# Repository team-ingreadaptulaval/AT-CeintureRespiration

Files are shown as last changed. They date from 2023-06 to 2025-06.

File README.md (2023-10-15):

# CeintureRespiration





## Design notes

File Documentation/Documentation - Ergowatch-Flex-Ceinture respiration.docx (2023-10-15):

### Carte principale

Pin arduino | Connection interne | Description
D0 | BTN4 (pas de pull-up)* | Bouton sur le PCB
D1 | BTN3 (pas de pull-up)* | Bouton sur le PCB
D2 | LED1 | LED sur le PCB
D3 | LED2 | LED sur le PCB
D4 | SD_DETECT | Carte SD insérée
D5 | EXT4 | Groove J2 pin 2
D6 | OLED_RST | Écran OLED et carte SD
D7 | OLED_CS | Écran OLED et carte SD
D8 | BUZZER | Buzzer sur le PCB
D9 | OLED_DC | Écran OLED et carte SD
D10 | SD_CS | Chip Select carte SD
D11 | SPI_MOSI | Écran OLED et carte SD
D12 | SPI_MISO | Écran OLED et carte SD
D13 | SPI_CLK | Écran OLED et carte SD
A0 | Batt_Voltage | diviseur de tension par 11
A1 | EXT1 | Groove J1 pin 1
A2 | EXT2 | Groove J1 Pin2
A3 | EXT3 | Groove J2 pin 1
A4 | SDA | Groove J3 pin 2
A5 | SCL | Groove J3 pin1
A6 | BTN1 (pas de pull-up)* | Bouton sur le PCB
A7 | BTN2 (pas de pull-up)* | Bouton sur le PCB
Vin | Batterie 9V | Alimente le arduino

*Utiliser la commande pinMode en INPUT_PULLUP

## Module d’expansion

Pin expansion | Connection | Module ceinture respiration
1 | GND
2 | VBAT | Recoit entre 4.5V et 9V
3 | EXT1 - A1 | Ceinture 1
4 | EXT2 - A2 | Ceinture 2
5 | EXT3 - A3
6 | EXT4 - D5
7 | SDA - A4
8 | SCL - A5
9 | 3V3
10 | 5V

## Carte Arduino installée

Carte 1 – Fabriquée le 23 septembre 2023

Arduino nano 33 sense REV2 –

https://docs.arduino.cc/hardware/nano-33-ble-sense-rev2

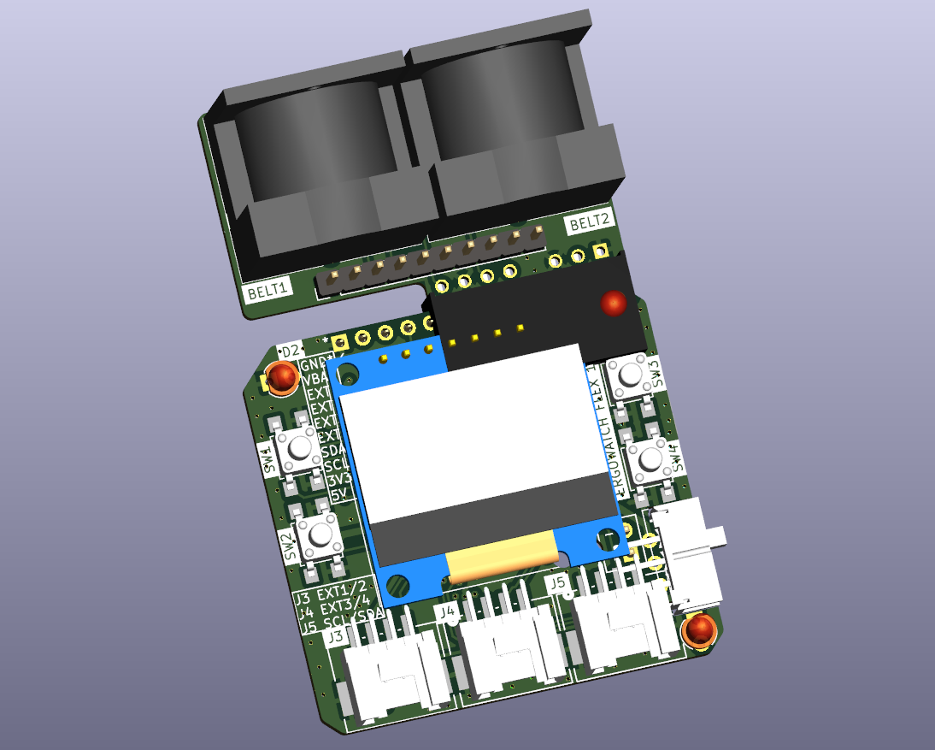
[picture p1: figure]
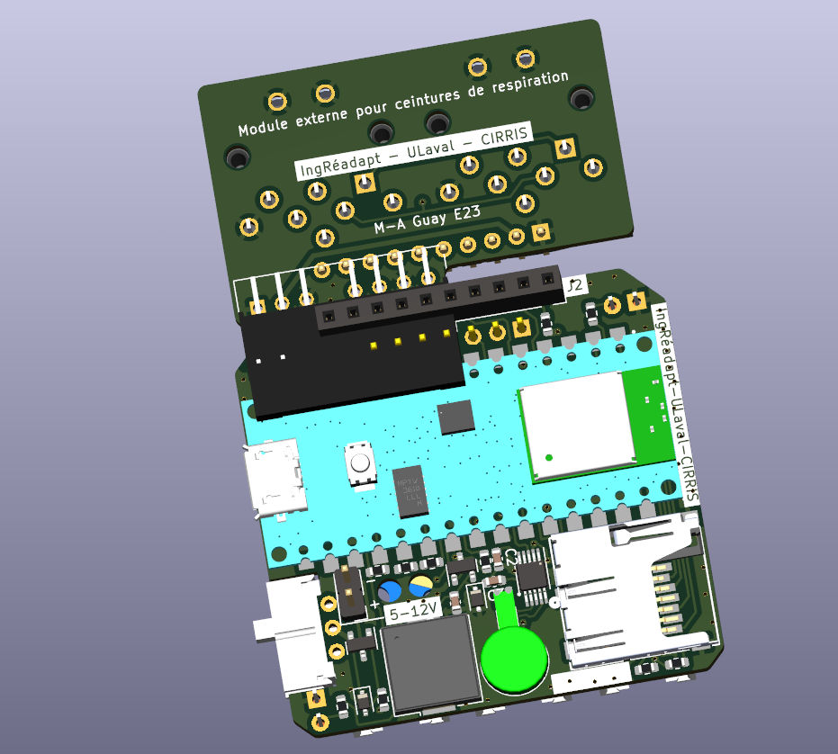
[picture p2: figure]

Documentation Ergowatch flex (Motherboard ceinture respiration)

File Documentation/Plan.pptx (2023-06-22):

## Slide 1

Batterie 12V

Bout on/off

Bout

LED

PQDE6W-Q24-D5-T

Bout

LED pwr

Connect
DIN

Arduino Nano 33 BLE

DRV &
VIB

Carte
SD

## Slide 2

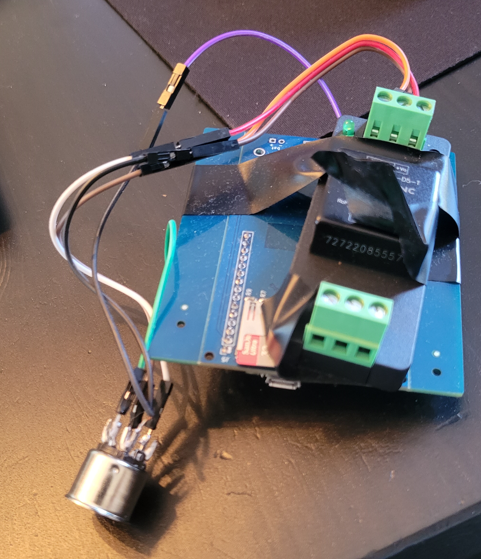
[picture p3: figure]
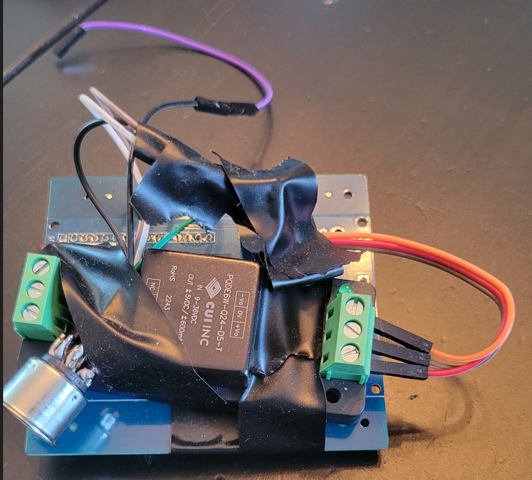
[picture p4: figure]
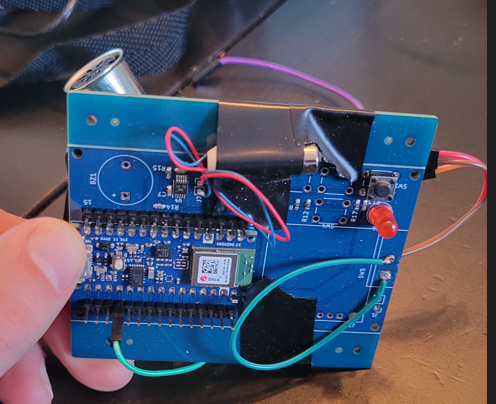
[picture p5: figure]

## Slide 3

GND arduino

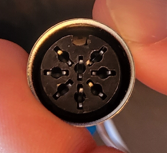
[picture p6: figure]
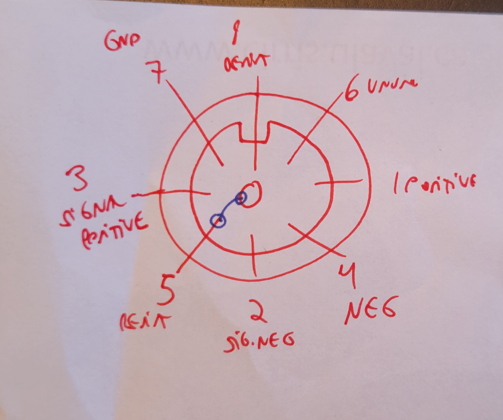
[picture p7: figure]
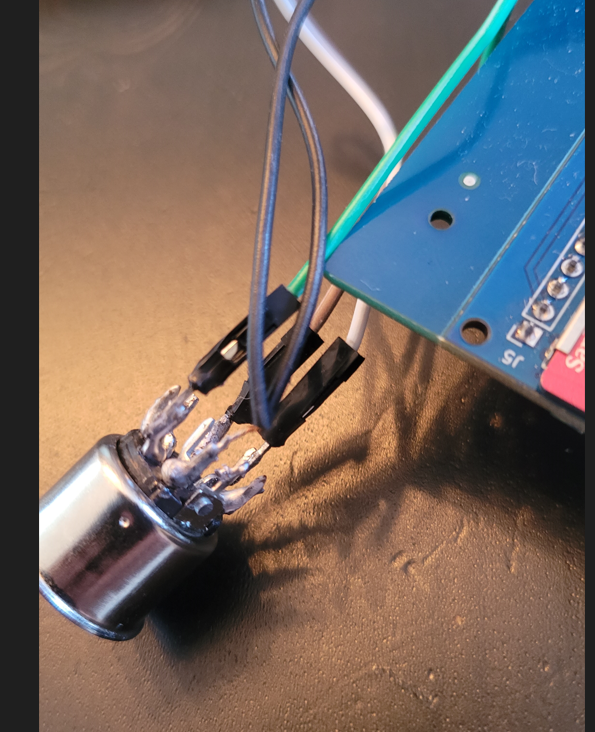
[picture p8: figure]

A0

PQDE6W-Q24-D5-T

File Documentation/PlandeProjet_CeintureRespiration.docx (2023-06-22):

# Plan de projet

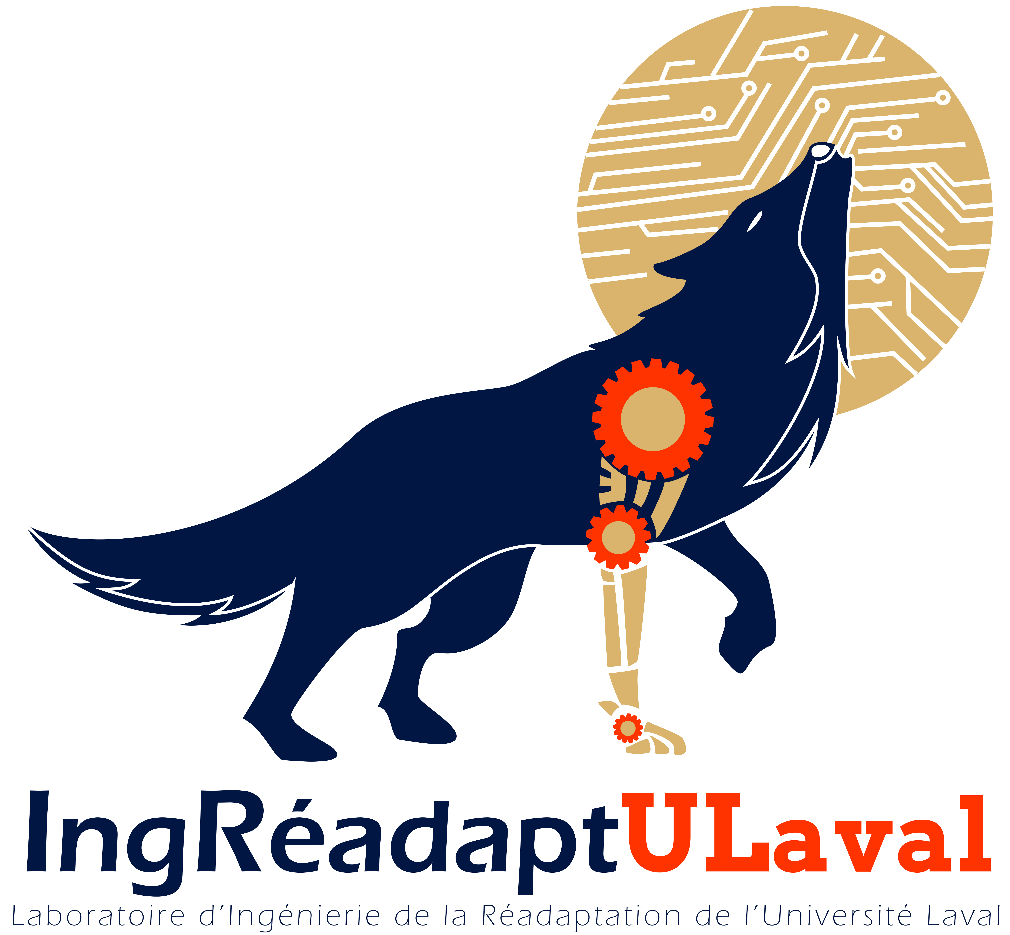
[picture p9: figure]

# Ceinture de respiration

Responsable de projet

Alexandre Campeau-Lecours, Marc-Antoine Guay, Simon Latour

Superviseurs

Simon Latour

Période : Été 2023

# 1 Sommaire du projet

## Introduction / énoncé du problème

Le projet consiste à développer une ceinture de respiration avec feedback, portable, pour des applications en orthophonie.

## Vision du projet

Un pré-prototype a déjà été réalisé par Alexandre Campeau-Lecours, en utilisant un PCB dérivé de montre de Simon Latour ainsi qu’une composante pour la régulation de tension +/-. Le capteur de respiration comme tel est acheté à l’externe et se connecte au connecteur DIN.

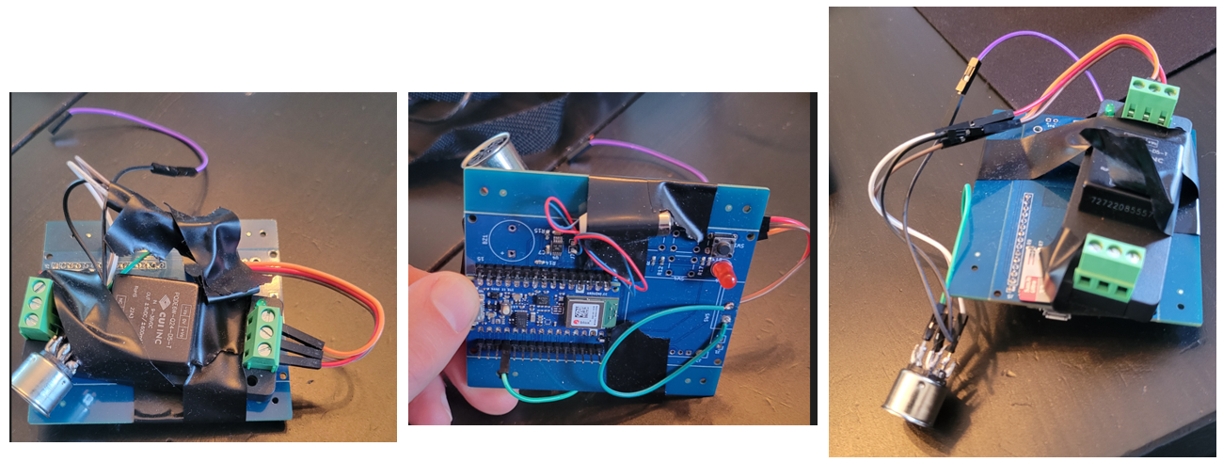
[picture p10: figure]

La version ci-haute était à un état de pré-prototype rudimentaire. Le but du projet actuel est de faire évoluer vers une version prototype mieux intégrée.
Celle-ci garderait les mêmes composantes (sauf possiblement le régulateur de tension +/- qui pourrait être remplacé par un autre modèle plus compact) tel que le Arduino Nano 33 BLE, mais de manière mieux intégrée et plus compacte (pas besoin d’optimiser en fou).

Sur le pré-prototype, l’alimentation est un bloc d’alimentation 12V, qui devrait devenir une batterie pour être portable. Un bouton switch d’alimentation on/off devrait également être ajouté.

Les composantes sont donc :

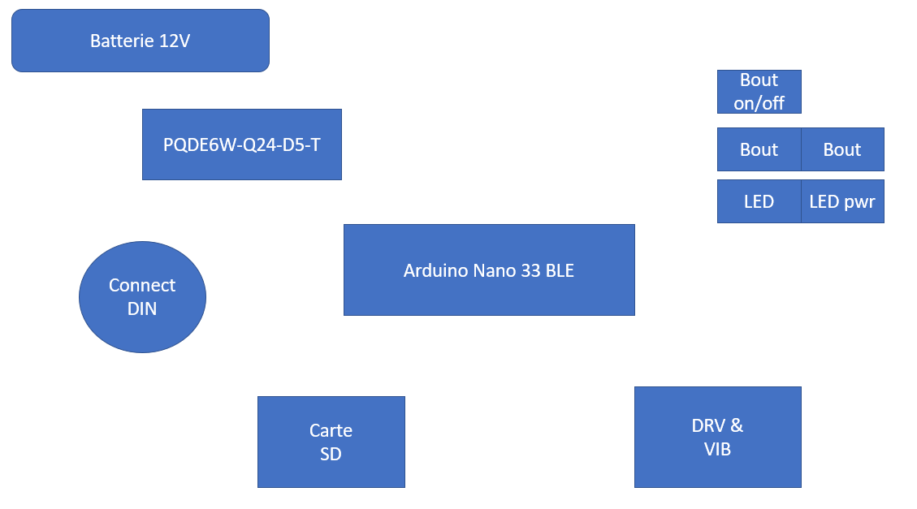
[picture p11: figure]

Il faudrait que la batterie puisse de recharger par des néophytes.

Autonomie visée de 4 ou 8hres.

Sur le prototype, il n’y avait qu’un connecteur DIN pour aller avec un capteur de respiration. Sur le board final, il faudrait deux connecteurs, pour que l’on puisse connecter deux capteur de respiration en même temps.

Le dossier du projet est situé ici :
R:\Projets\Recherche\ReadaptationDivers\RespirationCeintureMaude\PCBVersion1

Et voici le plan de branchement actuel

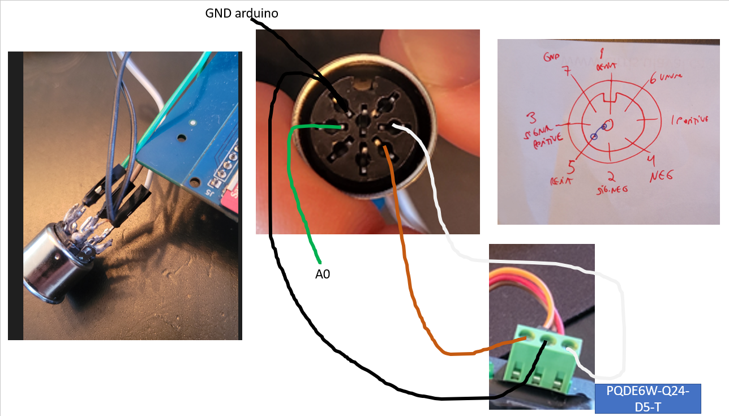
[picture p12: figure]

# 1 Méthode

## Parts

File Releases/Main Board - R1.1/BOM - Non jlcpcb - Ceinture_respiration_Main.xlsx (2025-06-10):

Reference | Value | Qty | LCSC | MPN | DNP | Exclude from BOM | Exclude from Board
A1 | Arduinon nano 33 ble R2 | 1
BT1 |  | 1 |  | BH9VPC / 36-232-ND | DNP | Excluded from BOM | Excluded from board
J3,J4,J5 | Conn_01x06_Pin | 3 |  | Grove Conn
J8 | Oled | 1 |  | AOM12864A0-0.96WW-ANO / ER-OLEDM0.96-1B-SPI-I2C
M1 | Motor_DC | 1 |  | VC0720B001F
S1 | EG1218 | 1 |  | EG1218

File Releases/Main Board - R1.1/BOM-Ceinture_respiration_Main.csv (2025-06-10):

Comment | Designator | Footprint | LCSC | Quantity
AP10N04S | Q2 | SOT-23 | C15127 | 1
1u | C2,C3 | C_0603_1608Metric | C15849 | 2
~ | LS1 | XDCR_CMT-7525-80-SMT-TR | C189208 | 1
D | D3 | D_SOD-323F | C191023 | 1
MMBT3904 | Q1 | SOT-23 | C20526 | 1
6-12V | D4 | D_SOD-323 | C2103 | 1
1K | R2,R3,R4,R7,R9 | R_0603_1608Metric | C21190 | 5
10K | R1,R10,R11,R5,R6,R8 | R_0603_1608Metric | C25804 | 6
500mA | F1,F2,F3 | Fuse_0603_1608Metric | C2844464 | 3
LED | D5 | LED_D3.0mm | C2895472 | 1
GREEN | D2 | LED_D3.0mm | C2895476 | 1
SW_Push | SW1,SW2,SW3,SW4 | SW_SPST_TL3305B | C2939211 | 4
MEM2061-01-188-00-A_REVA | J9 | GCT_MEM2061-01-188-00-A_REVA | C5151738 | 1
DRV2605LDGS | U1 | VSSOP-10_3x3mm_P0.5mm | C527464 | 1
RED | D1 | LED_D3.0mm | C779429 | 1
EG1218 | S1 | EG1218 |  | 1

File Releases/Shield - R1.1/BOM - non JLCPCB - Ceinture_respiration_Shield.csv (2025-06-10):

Reference | Value | Footprint | Datasheet | Qty | Digikey | LCSC | MPN | DNP | Exclude from BOM | Exclude from Board
J1 | Conn_01x10_Pin | Connector_PinHeader_2.54mm:PinHeader_1x10_P2.54mm_Vertical | ~ | 1 | 2553-2011-1X10G00SB-ND | C492409 | 2011-1X10G00SB
J6,J7 | DIN-8 | CentureResp:CUI_SDS-80J | http://www.mouser.com/ds/2/18/40_c091_abd_e-75918.pdf | 2 | CP-2380-ND |  | SDS-80J
PS1 | RS3-0505D | CONV_RS3-0505D |  | 1 | 945-1318-ND | C46594429

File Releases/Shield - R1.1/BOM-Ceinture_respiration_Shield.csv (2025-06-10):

Comment | Designator | Footprint | LCSC | Quantity
Conn_01x10_Pin | J1 | PinHeader_1x10_P2.54mm_Vertical | C492409 | 1
DIN-8 | J6,J7 | CUI_SDS-80J | C5382951 | 2
RS3-0505D | PS1 | CONV_RS3-0505D | C5870380 | 1

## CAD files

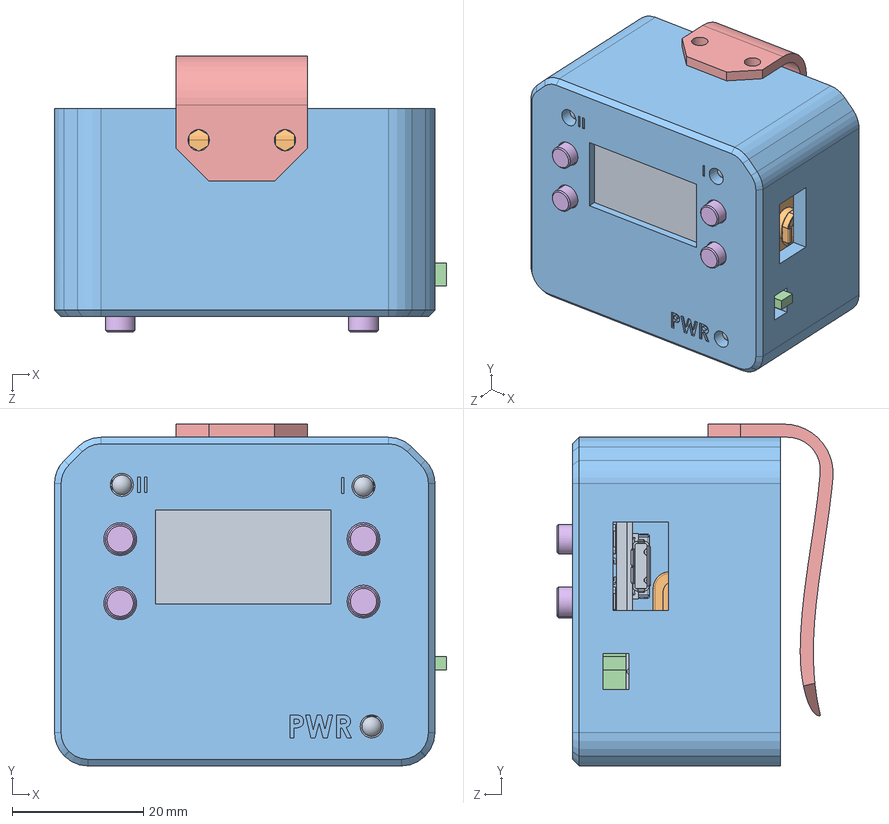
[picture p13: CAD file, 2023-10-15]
CAD Boitier/Assy-PCB_noDin/AT005-ASSY.SLDASM
59.6 x 52.0 x 42.0 mm
AT005-Main-PCB
9V-battery
AT0005-Case-Main
Interrupteur
AT005-Clip
AT005-Bouton x 4

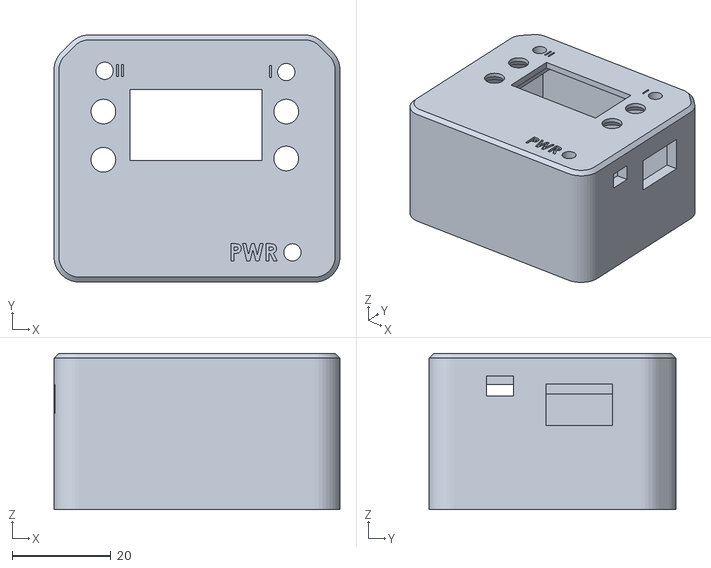
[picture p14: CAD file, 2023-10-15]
CAD Boitier/Assy-PCB_noDin/Production/Prod 3/AT0005-Case-Main.STL
57.9 x 50.0 x 31.7

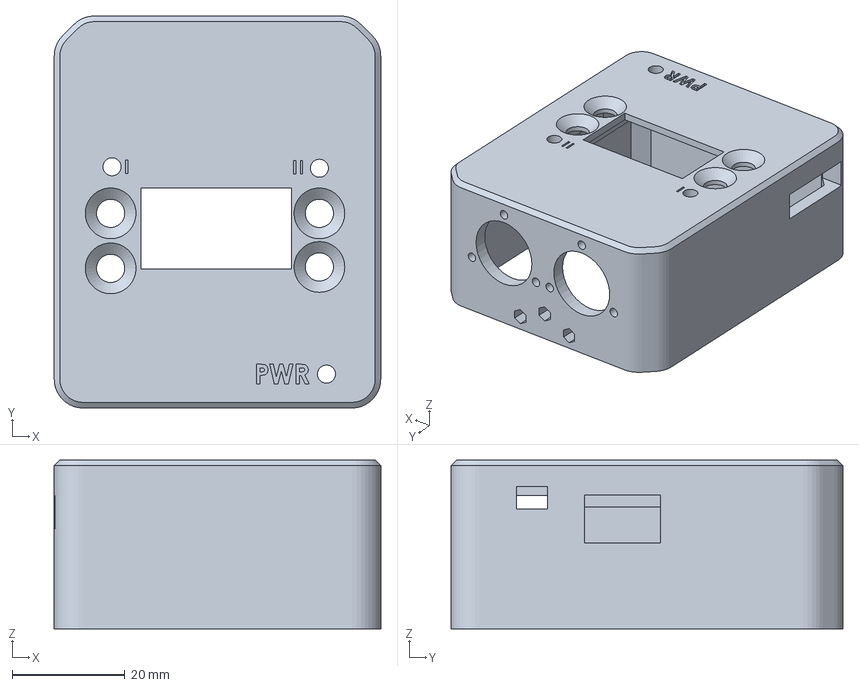
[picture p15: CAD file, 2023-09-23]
CAD Boitier/Assy-PCB_noDin/Production/Prod 1/AT0005-Case-Main.3MF
57.9 x 69.5 x 29.9 mm

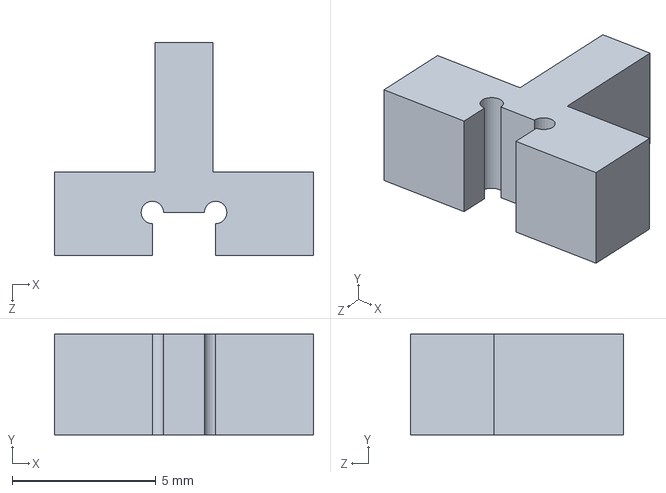
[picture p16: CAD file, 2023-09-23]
CAD Boitier/Assy-PCB_noDin/Production/Interrupteur.SLDPRT
9.00 x 3.50 x 7.41 mm

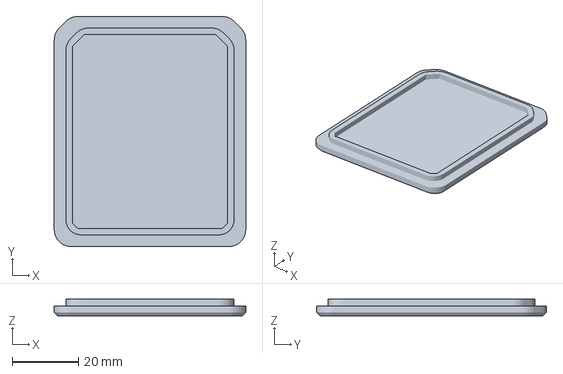
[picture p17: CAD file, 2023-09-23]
CAD Boitier/Assy-PCB_noDin/Production/Prod 1/AT005-Couvercle.3MF
57.9 x 69.5 x 5.00 mm

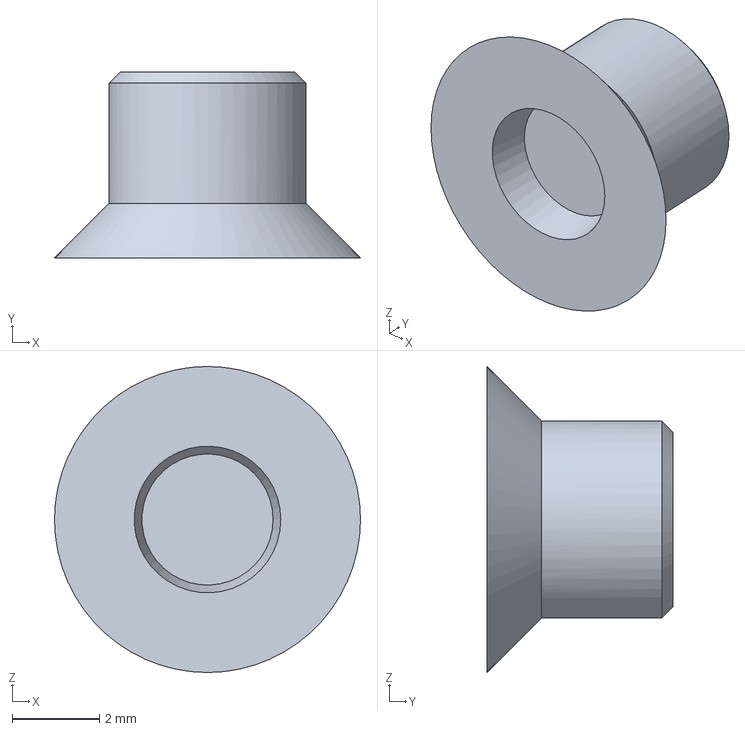
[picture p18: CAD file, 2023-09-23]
CAD Boitier/Assy-PCB_noDin/Production/Prod 2/AT005-Bouton.3MF
7.00 x 4.25 x 7.00 mm

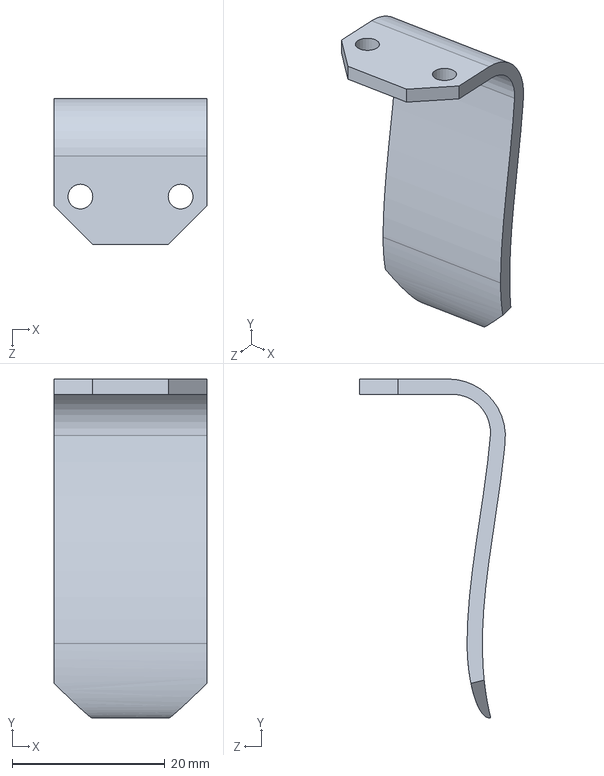
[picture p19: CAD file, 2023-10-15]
CAD Boitier/Assy-PCB_noDin/AT005-Clip.SLDPRT
20.0 x 44.4 x 19.1 mm

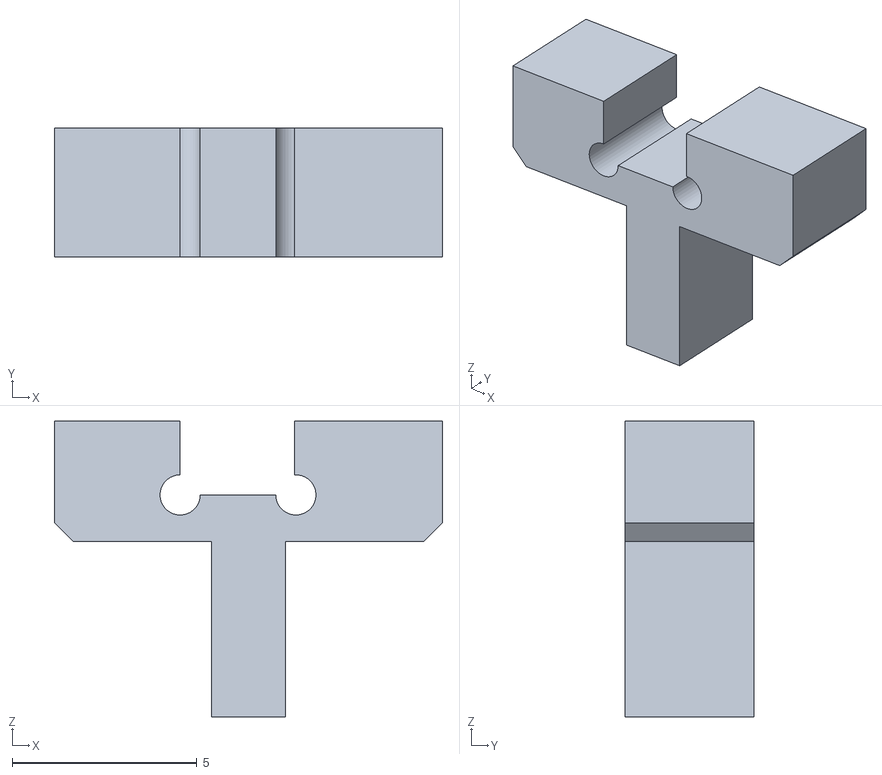
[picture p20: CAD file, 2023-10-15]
CAD Boitier/Assy-PCB_noDin/Production/Prod 3/AT005-Interrupteur.STL
10.5 x 3.50 x 8.01

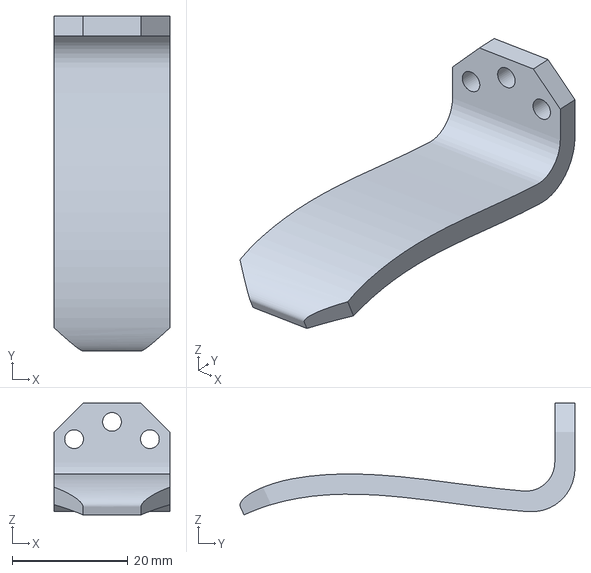
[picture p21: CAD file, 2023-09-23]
CAD Boitier/Assy-PCB_noDin/Production/Prod 1/AT005-Clip.3MF
20.0 x 58.0 x 19.4 mm

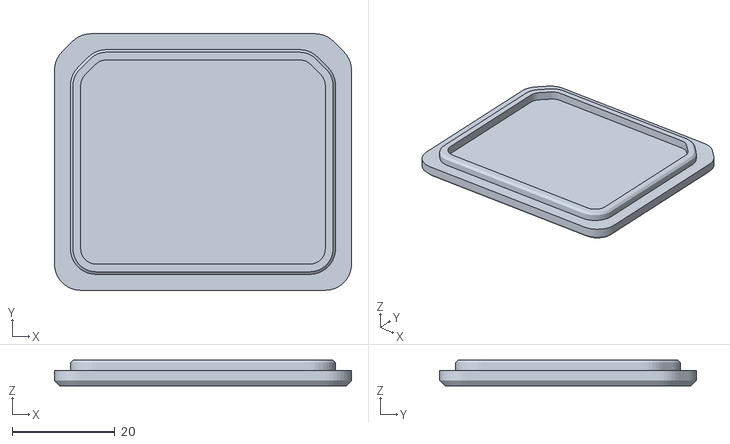
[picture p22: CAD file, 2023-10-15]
CAD Boitier/Assy-PCB_noDin/Production/Prod 3/AT005-Couvercle.STL
57.9 x 50.0 x 5.00

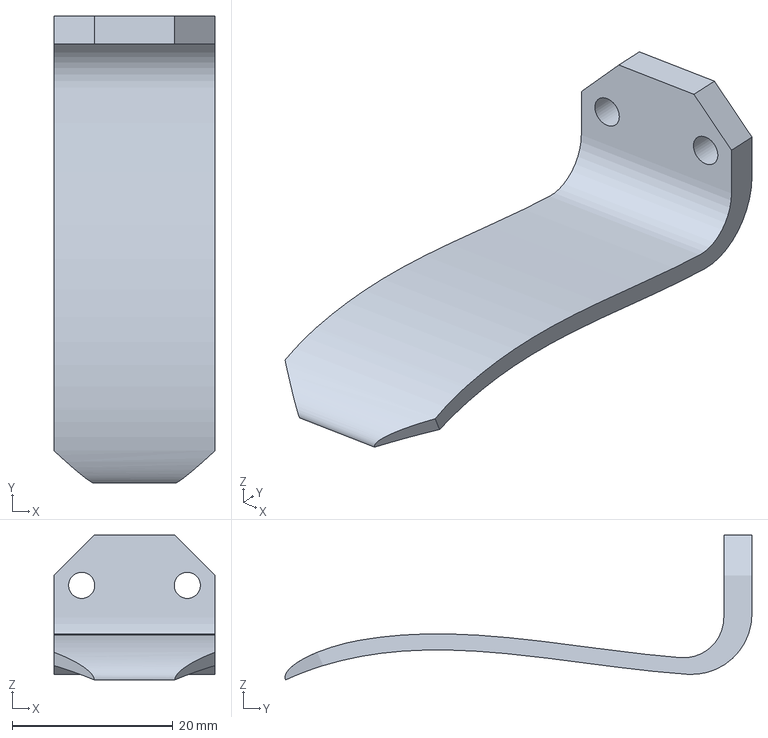
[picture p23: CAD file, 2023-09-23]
CAD Boitier/Assy-PCB_noDin/Production/Prod 2/AT005-Clip.3MF
20.0 x 58.0 x 18.0 mm

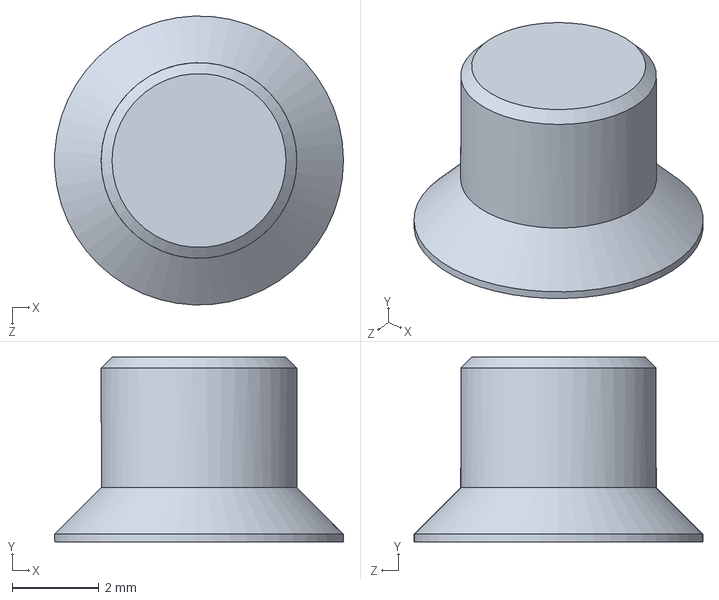
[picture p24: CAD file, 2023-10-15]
CAD Boitier/Assy-PCB_noDin/AT005-Bouton.SLDPRT
6.65 x 4.25 x 6.64 mm

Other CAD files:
CAD Boitier/Assy-PCB_noDin/Production/Prod 2/AT0005-Case-Main.3MF
CAD Boitier/Assy-PCB_noDin/AT0005-Case-Main.SLDPRT
CAD Boitier/Assy-PCB_noDin/Production/Prod 2/AT005-Couvercle.3MF
CAD Boitier/Assy-PCB_noDin/Interrupteur.SLDPRT
CAD Boitier/Assy-PCB_noDin/Production/Prod 1/AT005-Interrupteur.3MF
CAD Boitier/Assy-PCB_noDin/Production/Prod 3/AT005-Clip.STL
CAD Boitier/Assy-PCB_noDin/9V-battery.SLDPRT
CAD Boitier/Assy-PCB_noDin/AT005-Couvercle.SLDPRT
CAD Boitier/Assy-PCB_noDin/AT005-Shield-PCB.SLDPRT
CAD Boitier/Assy-PCB_noDin/Production/Prod 2/Interrupteur.3MF
CAD Boitier/Assy-PCB_noDin/Production/Prod 3/AT005-Bouton.STL

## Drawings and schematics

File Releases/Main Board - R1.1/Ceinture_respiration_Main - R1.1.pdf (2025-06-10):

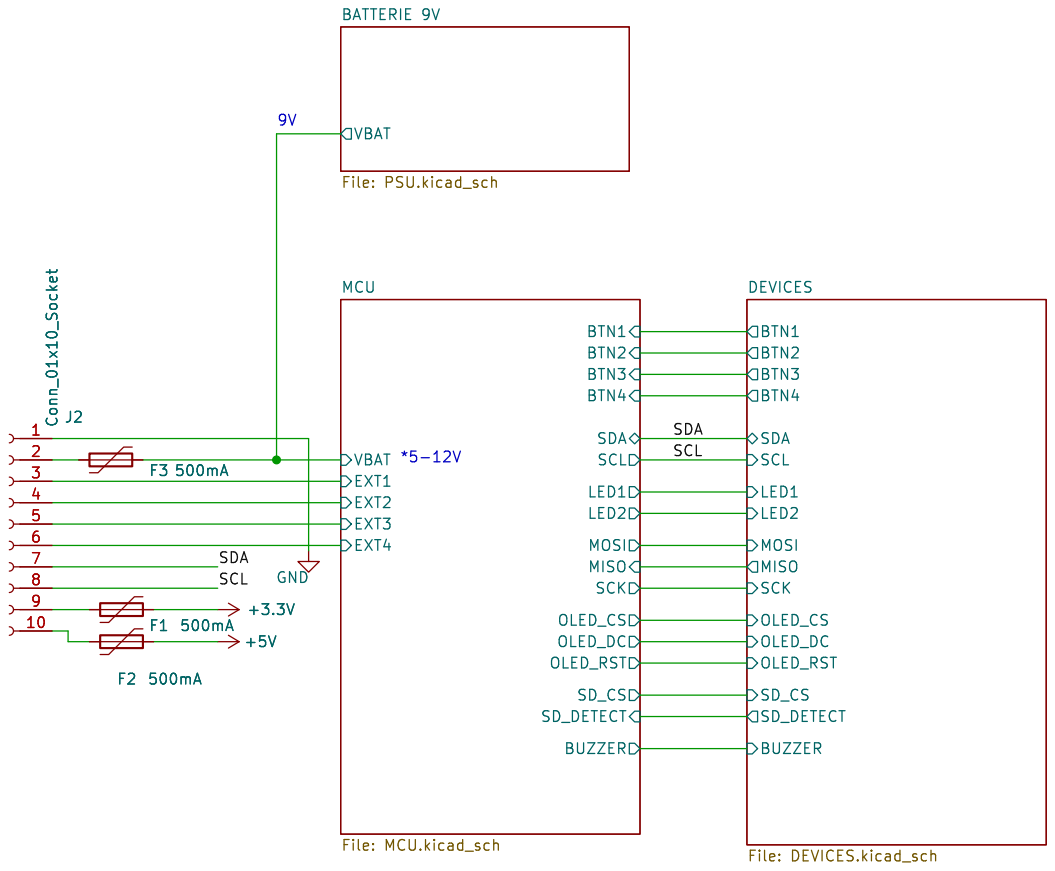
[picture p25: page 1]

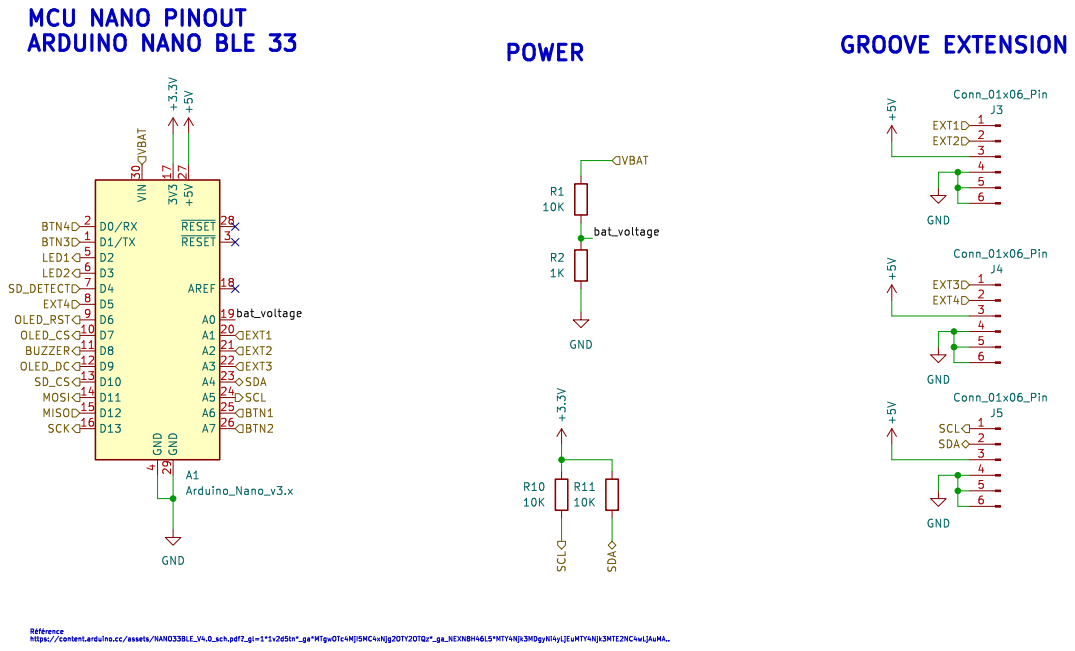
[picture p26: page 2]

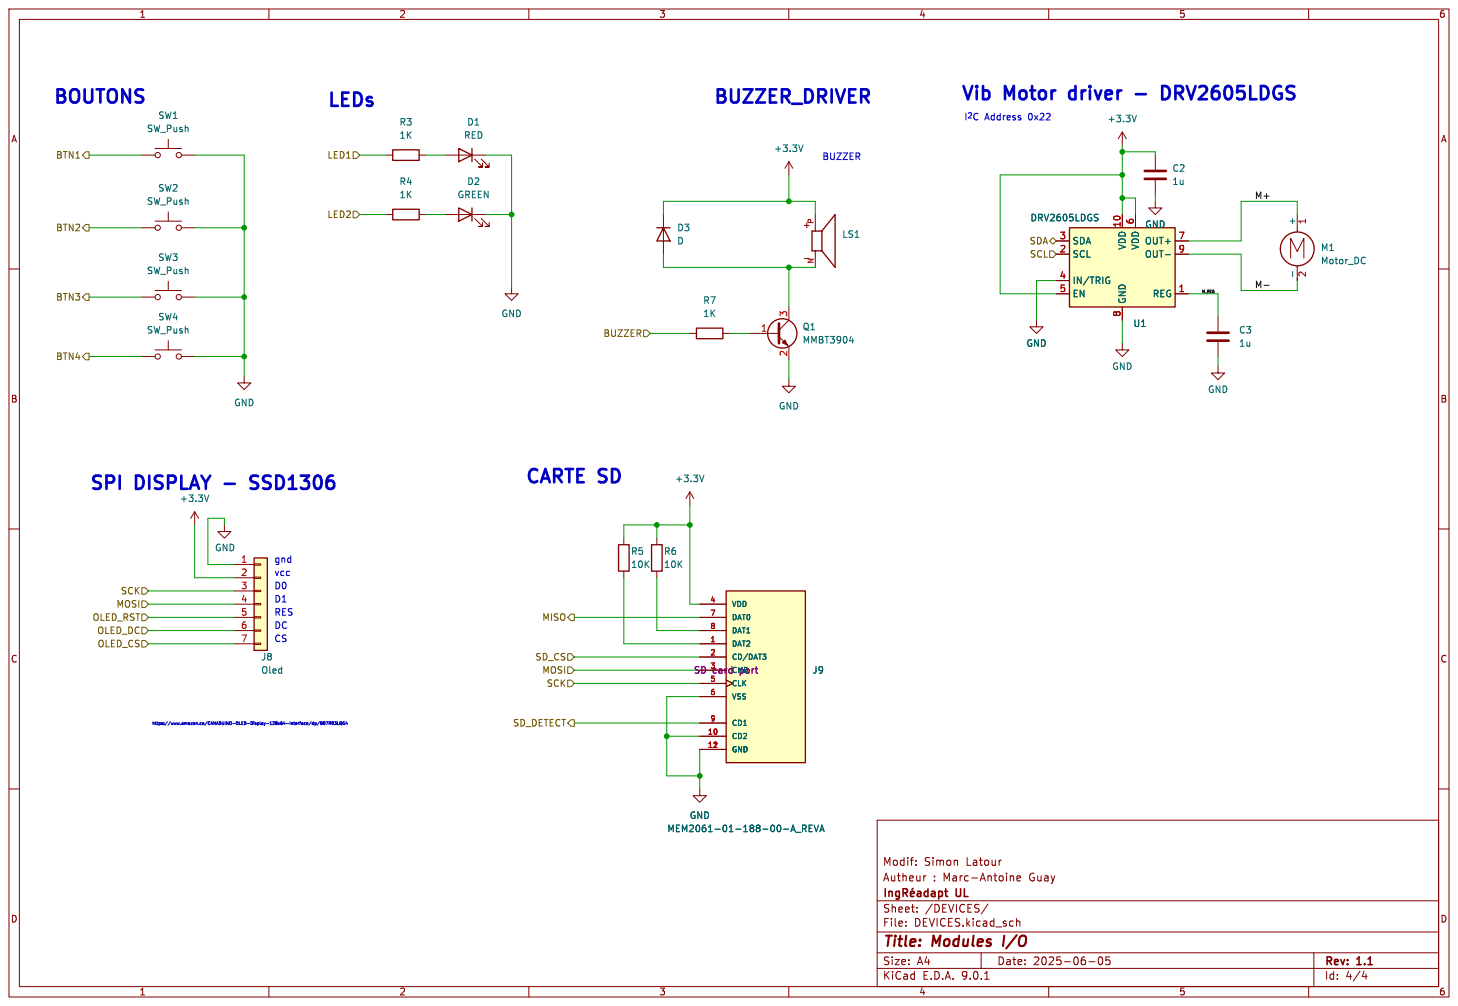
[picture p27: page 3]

I^{2}CAddress 0x22 Vib Motor driver - DRV2605LDGS

6 OUT+ 7 OUT- 9 REG 1 GND GND

https://www.amazon.ca/CANADUINO-OLED-Display-128x64-Interface/dp/B07R93LQG4

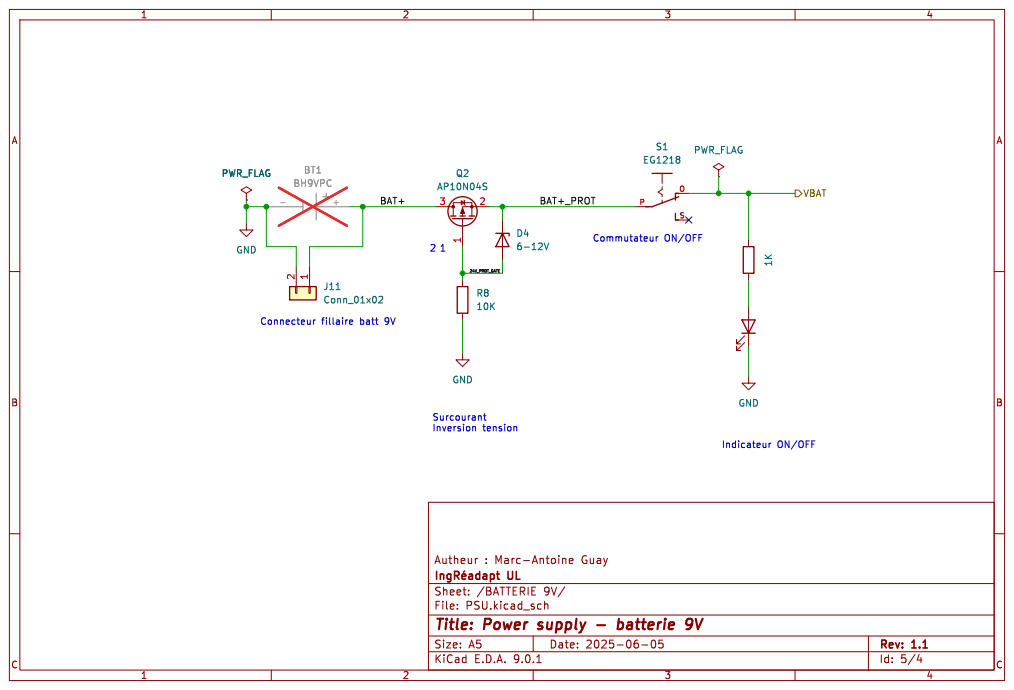
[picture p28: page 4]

Id: 5/4 Title: Power supply - batterie 9V

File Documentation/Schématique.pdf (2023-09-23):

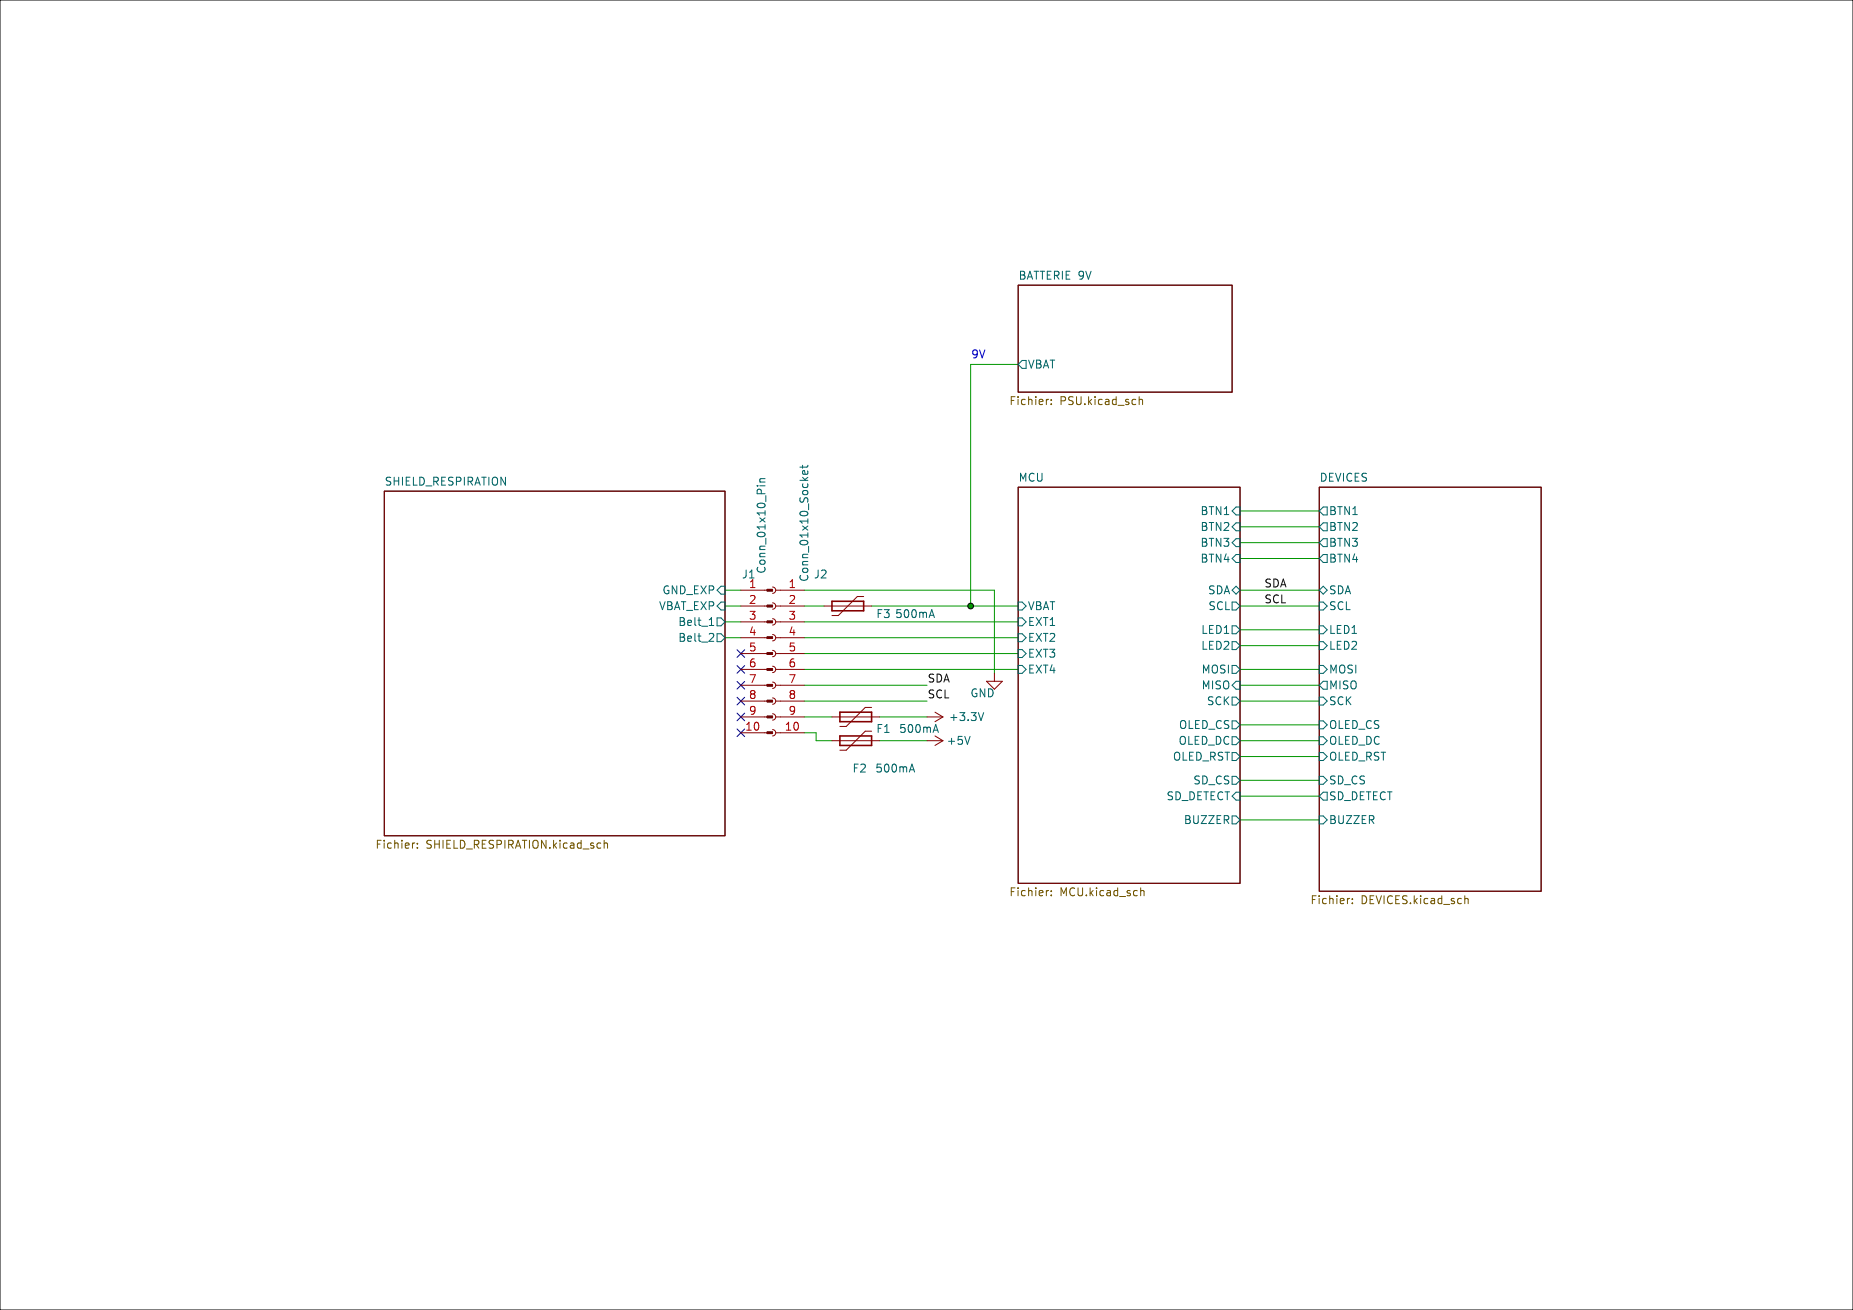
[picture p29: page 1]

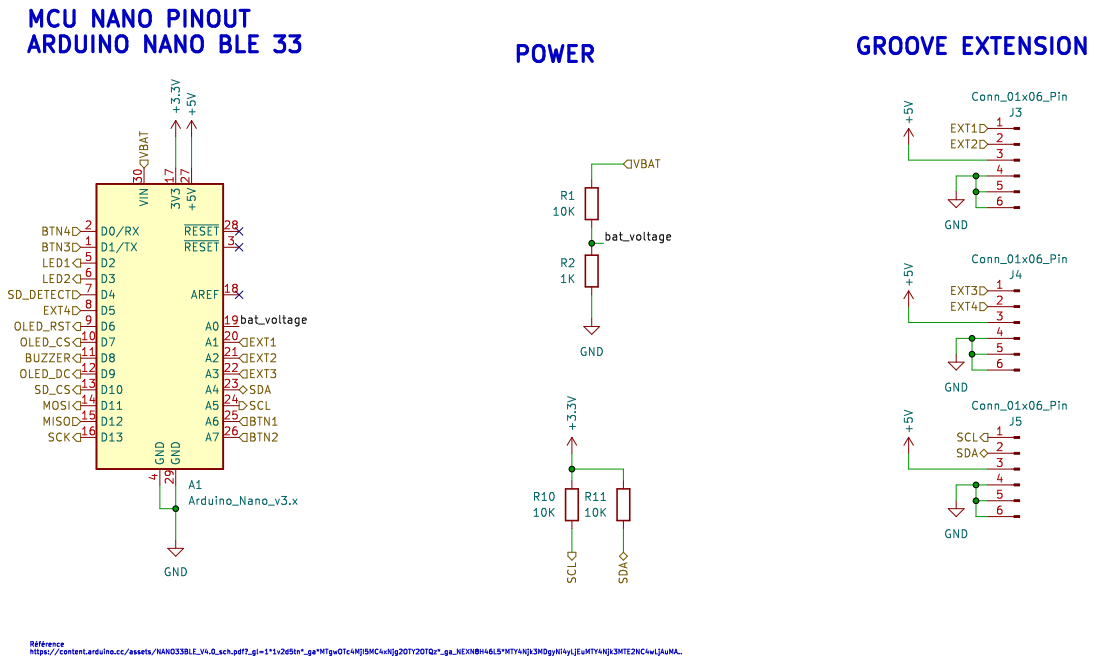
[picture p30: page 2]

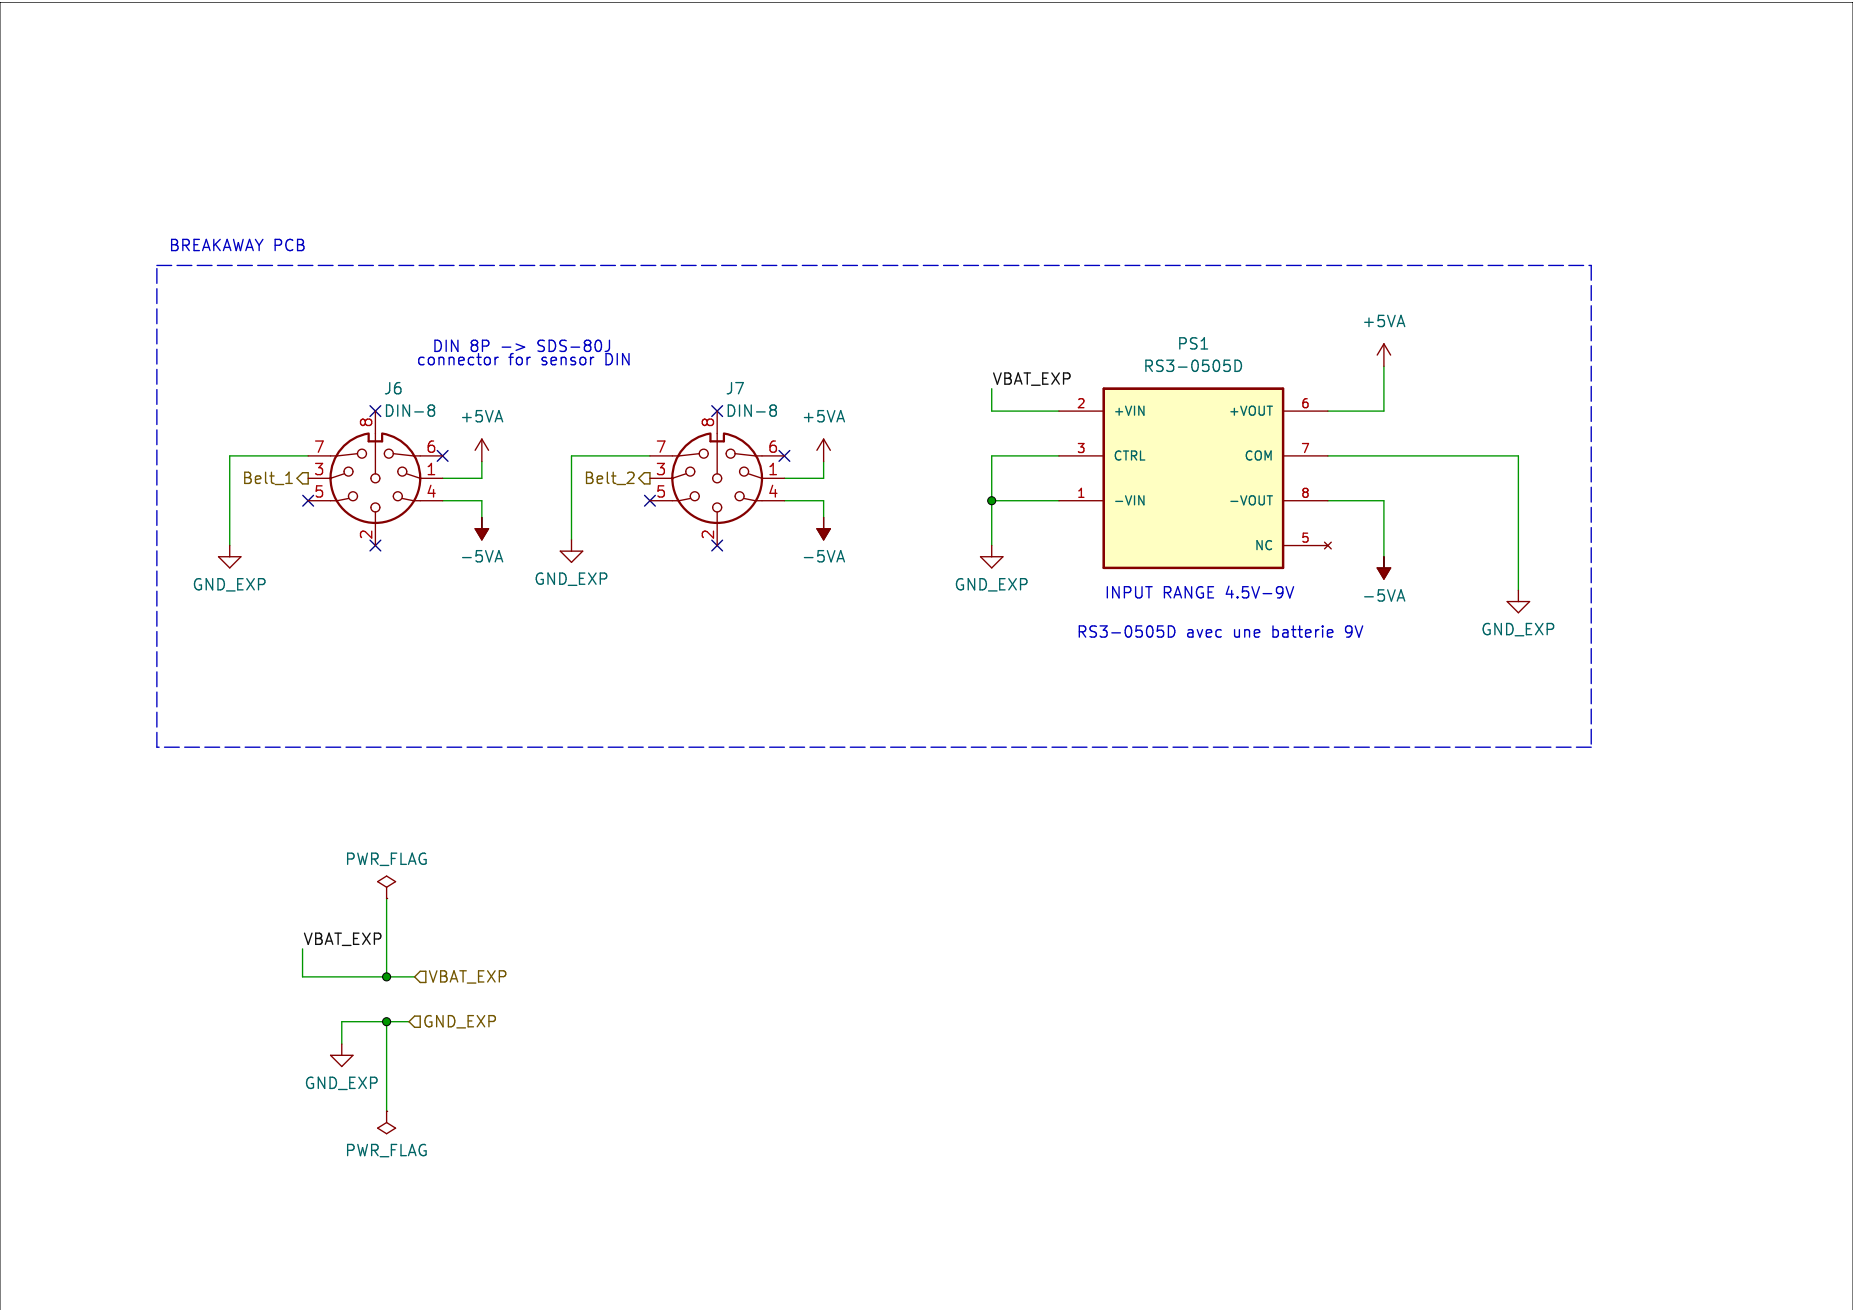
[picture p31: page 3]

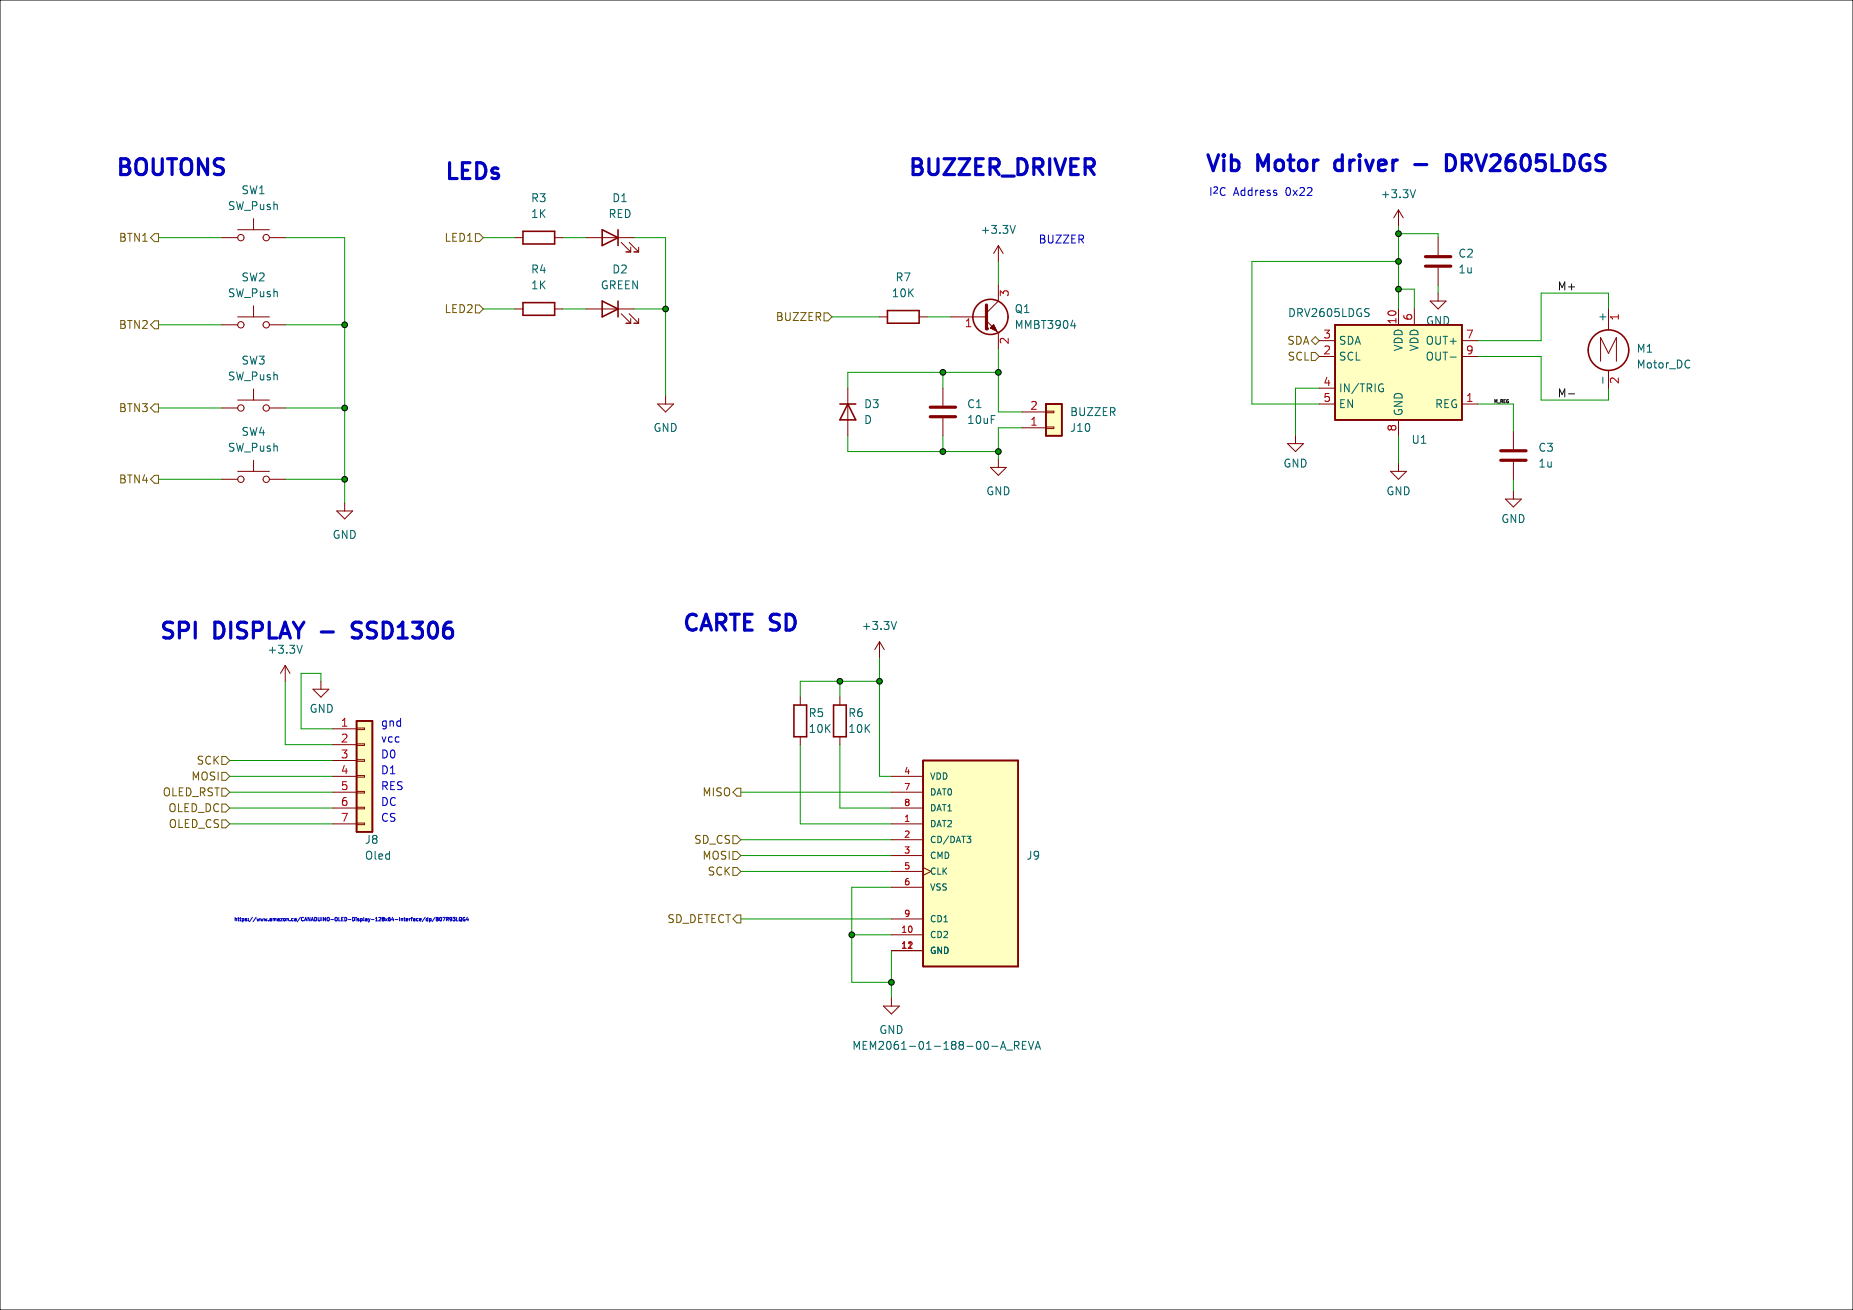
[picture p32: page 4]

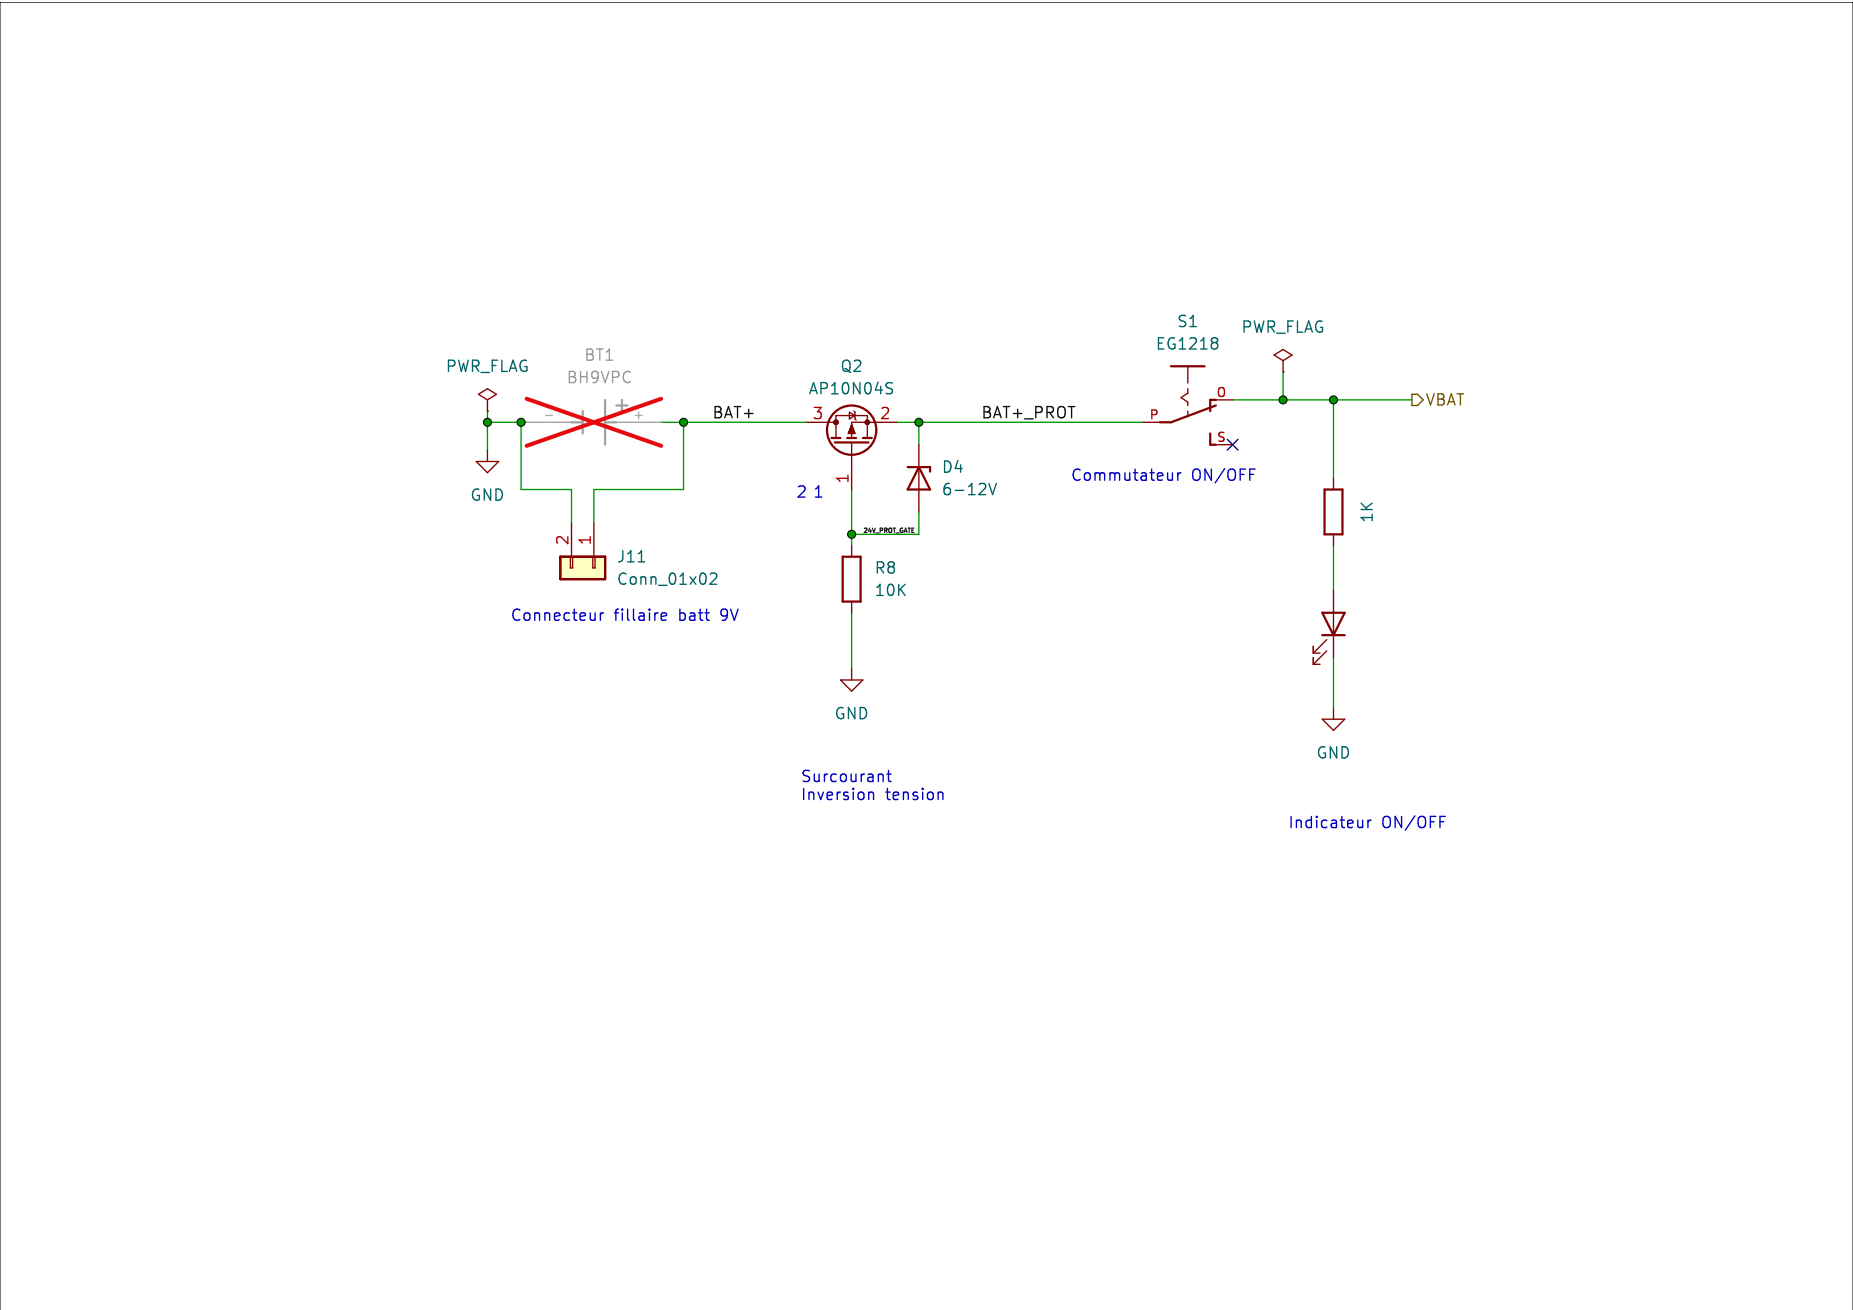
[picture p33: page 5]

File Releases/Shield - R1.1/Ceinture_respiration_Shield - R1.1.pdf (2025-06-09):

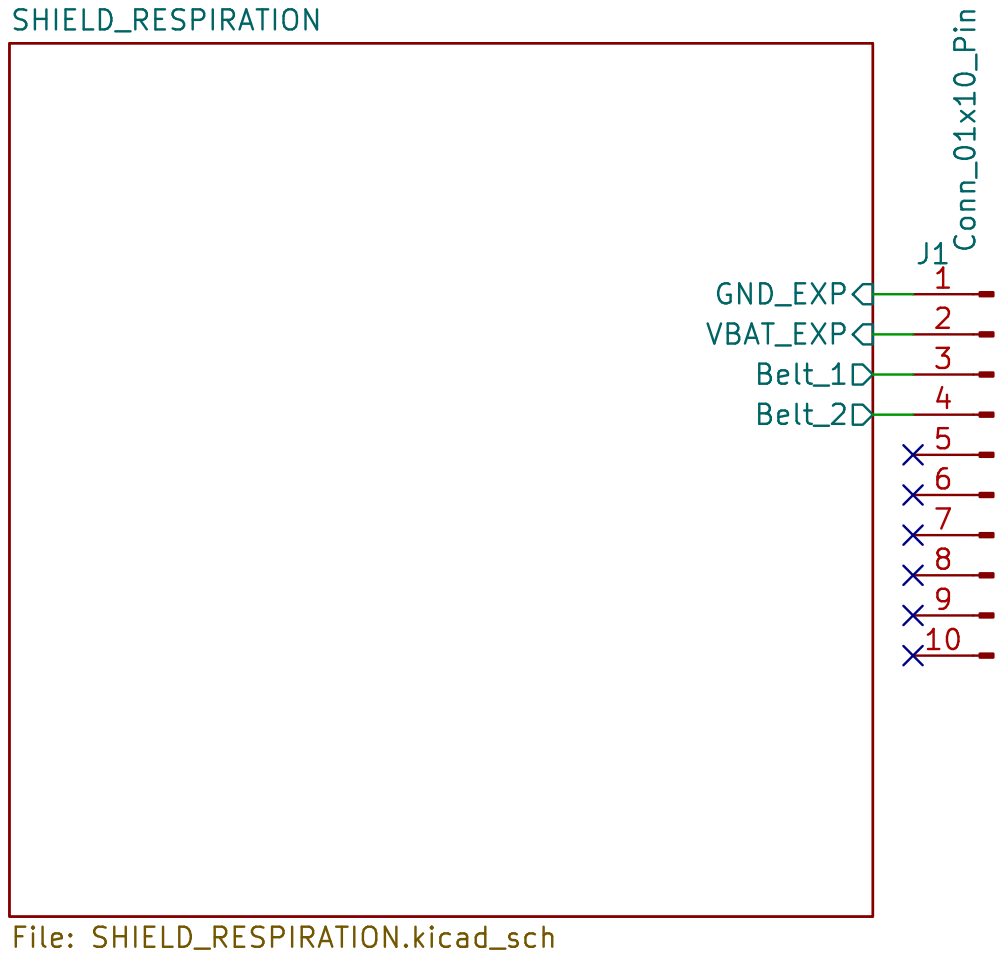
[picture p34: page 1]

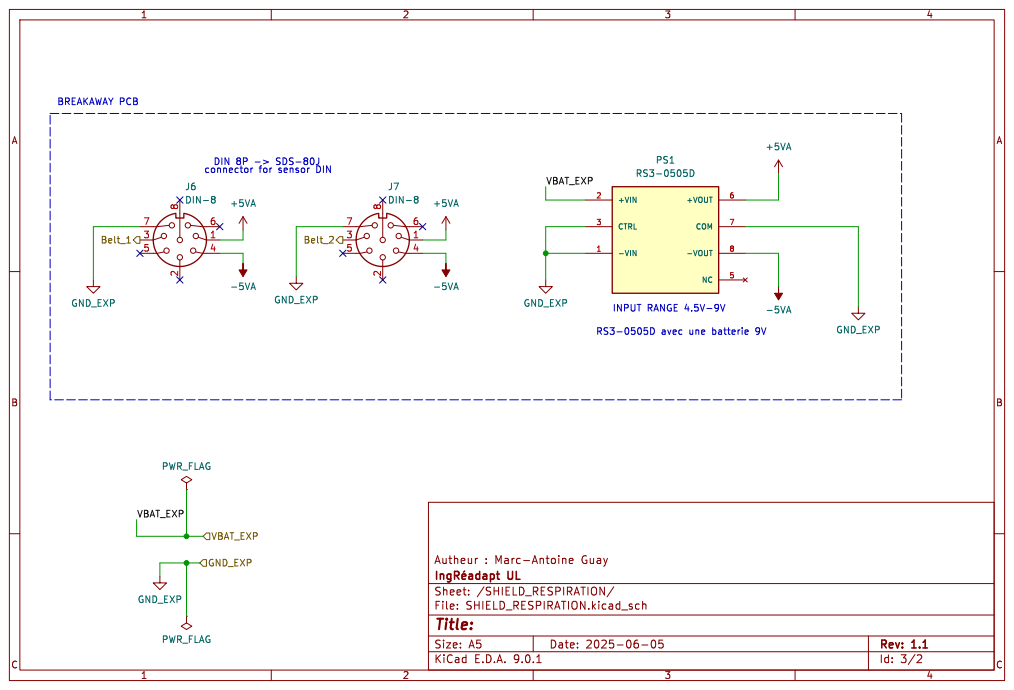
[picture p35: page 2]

Id: 3/2 Title: File: SHIELD_RESPIRATION.kicad_sch Sheet: /SHIELD_RESPIRATION/

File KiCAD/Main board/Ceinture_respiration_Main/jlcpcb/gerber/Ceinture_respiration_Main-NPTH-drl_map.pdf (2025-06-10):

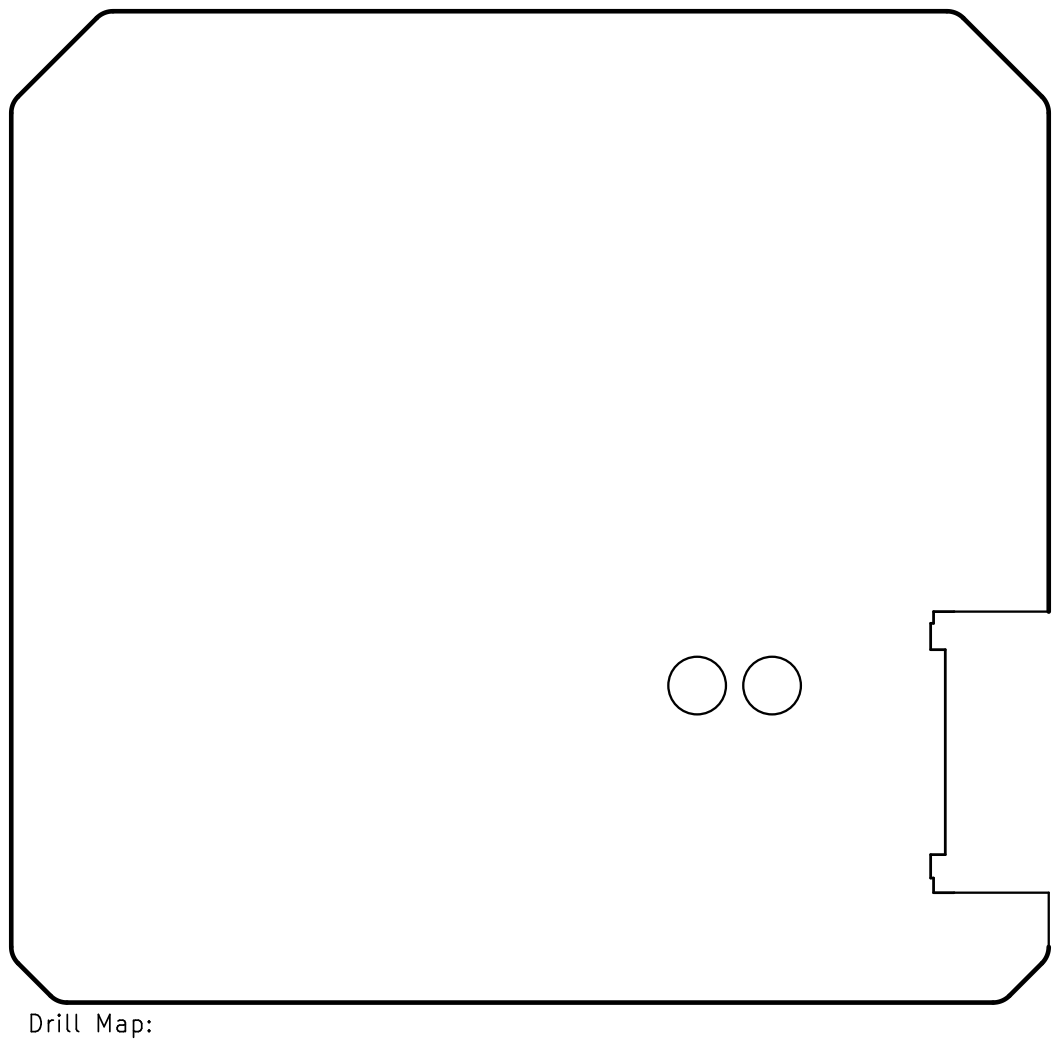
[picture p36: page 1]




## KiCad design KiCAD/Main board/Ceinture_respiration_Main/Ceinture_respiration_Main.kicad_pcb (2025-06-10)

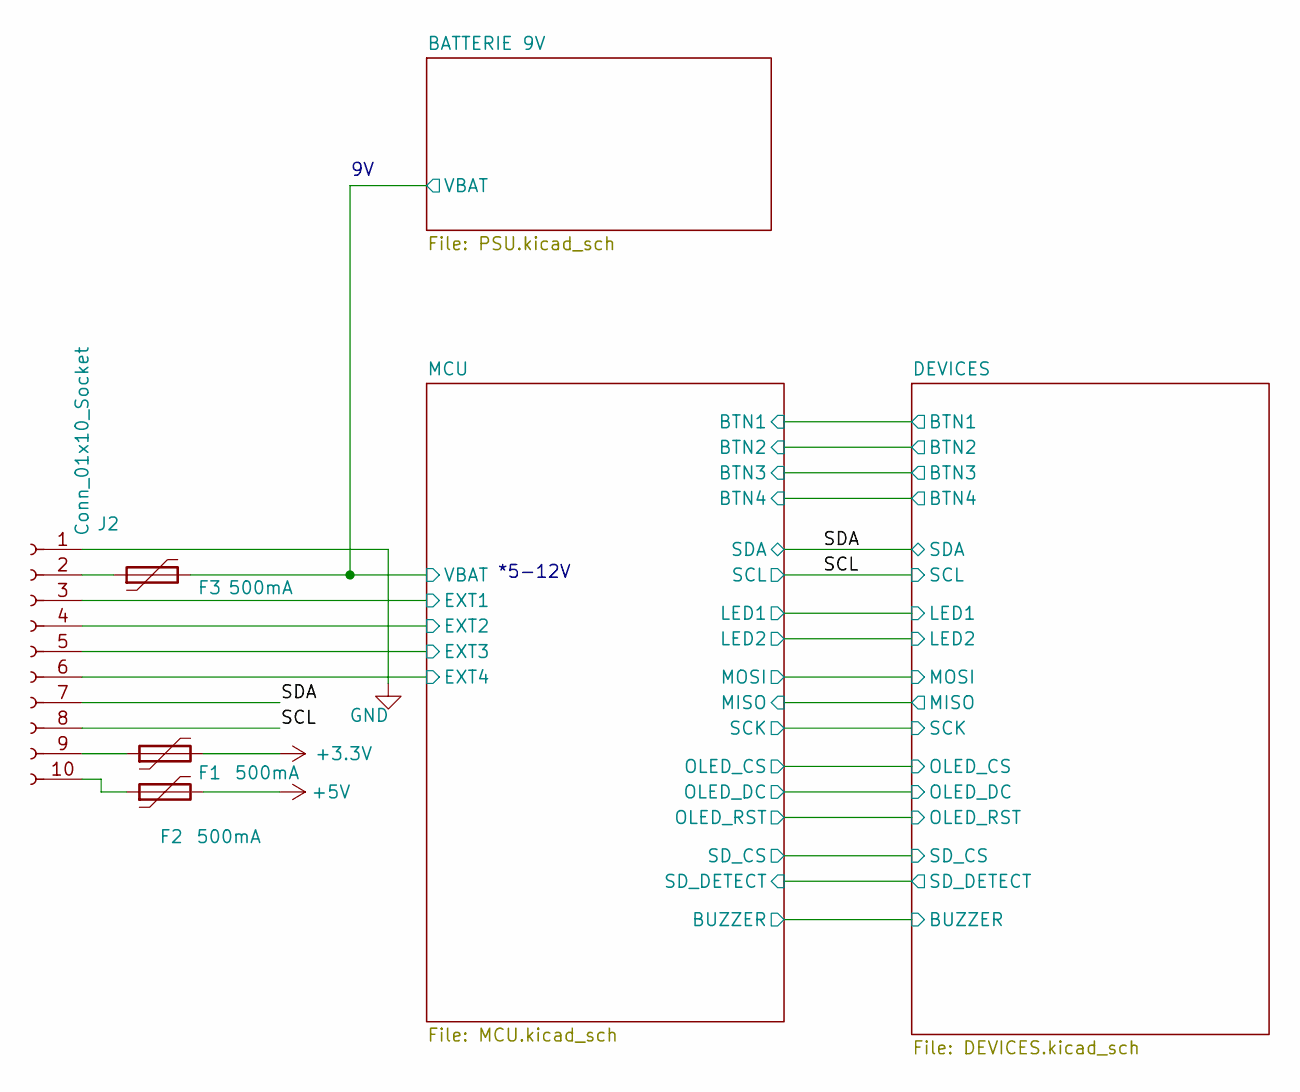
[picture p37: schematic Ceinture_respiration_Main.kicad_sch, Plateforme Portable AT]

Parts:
F1, F2, F3: 500mA; Fuse_0603_1608Metric; LCSC C2844464
J2: Conn_01x10_Socket; PinSocket_1x10_P2.54mm_Vertical; LCSC C2897373

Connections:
+3.3V: F1.2; also elsewhere on the board
+5V: F2.2; also elsewhere on the board
/BATTERIE 9V/VBAT: F3.2; also elsewhere on the board
/MCU/EXT1: J2.3; also elsewhere on the board
/MCU/EXT2: J2.4; also elsewhere on the board
/MCU/EXT3: J2.5; also elsewhere on the board
/MCU/EXT4: J2.6; also elsewhere on the board
/SCL: J2.8; also elsewhere on the board
/SDA: J2.7; also elsewhere on the board
GND: J2.1; also elsewhere on the board
unnamed: F3.1, J2.2
unnamed: F1.1, J2.9
unnamed: F2.1, J2.10

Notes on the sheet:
*5-12V

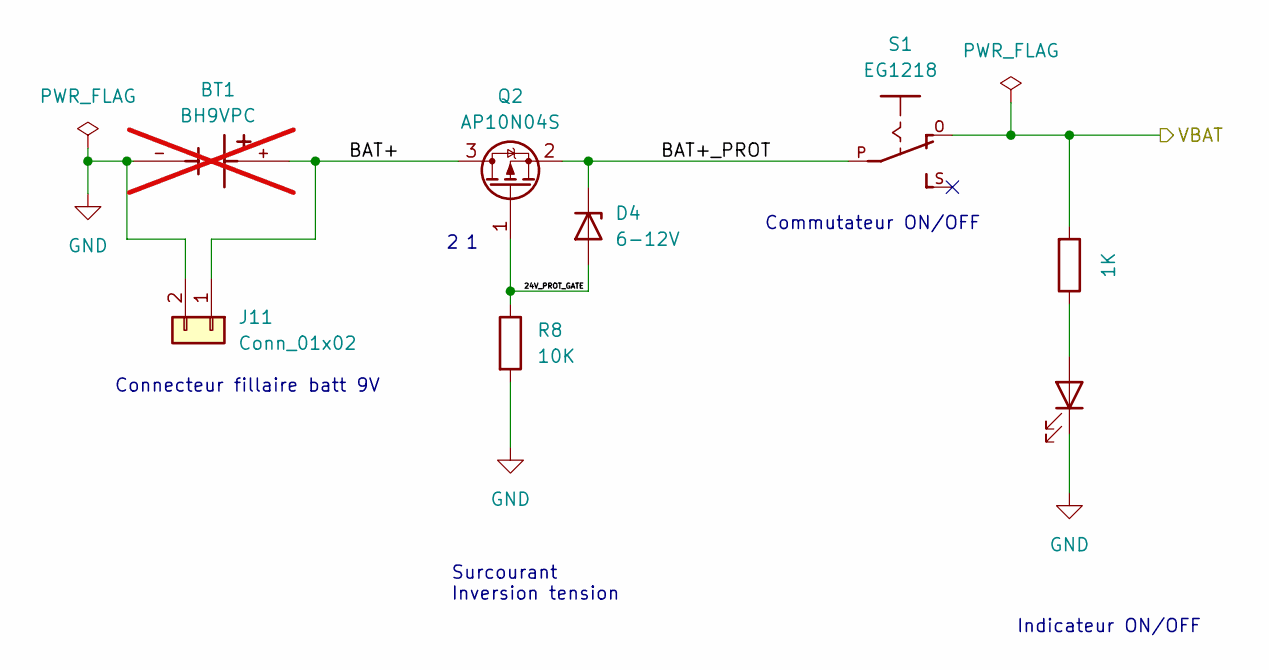
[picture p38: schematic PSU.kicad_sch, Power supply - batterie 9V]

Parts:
BT1: BH9VPC; BAT_BH9VPC; PARTREV F; not fitted
D4: 6-12V; D_SOD-323; LCSC C2103
D5: LED; LED_D3.0mm; LCSC C2895472
J11: Conn_01x02; PinHeader_1x02_P2.54mm_Vertical
Q2: AP10N04S; SOT-23; LCSC C15127
R8: 10K; R_0603_1608Metric; LCSC C25804
R9: 1K; R_0603_1608Metric; LCSC C21190
S1: EG1218; MPN EG1218; DigiKey EG1218

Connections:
/BATTERIE 9V/24V_PROT_GATE: D4.2 (A), Q2.1 (G), R8.1
/BATTERIE 9V/BAT+: J11.1, Q2.3 (D)
/BATTERIE 9V/BAT+_PROT: D4.1 (K), Q2.2 (S), S1.P
/BATTERIE 9V/VBAT: R9.2, S1.O; also elsewhere on the board
GND: D5.1 (K), J11.2, R8.2; also elsewhere on the board
unnamed: D5.2 (A), R9.1

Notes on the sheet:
Connecteur fillaire batt 9V
Commutateur ON/OFF
Indicateur ON/OFF
Surcourant Inversion tension

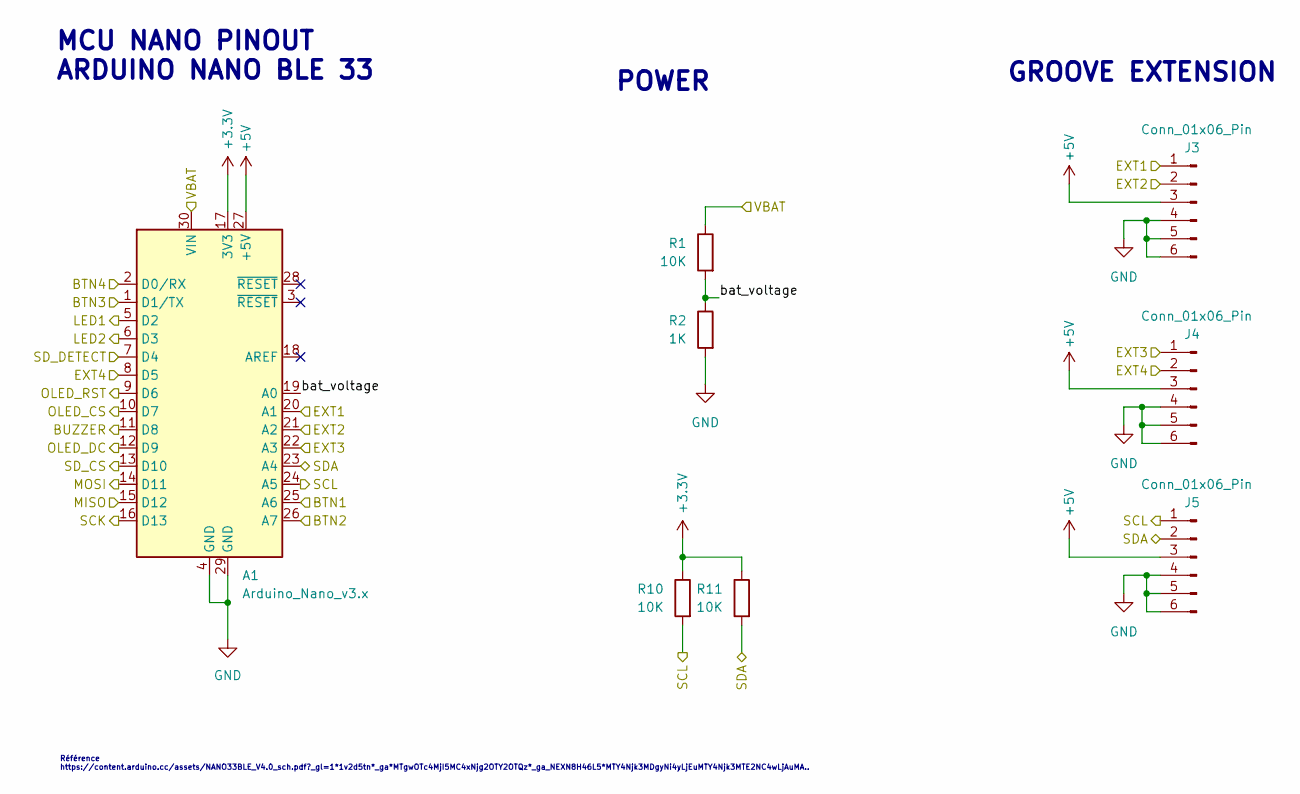
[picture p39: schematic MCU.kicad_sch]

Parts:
A1: Arduino_Nano_v3.x; MODULE_ABX00027
J3, J4, J5: Conn_01x06_Pin; CONN4_20164_SEE; MPN Grove Conn
R1, R10, R11: 10K; R_0603_1608Metric; LCSC C25804
R2: 1K; R_0603_1608Metric; LCSC C21190

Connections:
+3.3V: A1.17 (3V3), R10.1, R11.1; also elsewhere on the board
+5V: A1.27 (+5V), J3.3, J4.3, J5.3; also elsewhere on the board
/BATTERIE 9V/VBAT: A1.30 (VIN), R1.1; also elsewhere on the board
/DEVICES/BTN1: A1.25 (A6); also elsewhere on the board
/DEVICES/BTN2: A1.26 (A7); also elsewhere on the board
/DEVICES/BTN3: A1.1 (D1/TX); also elsewhere on the board
/DEVICES/BTN4: A1.2 (D0/RX); also elsewhere on the board
/DEVICES/BUZZER: A1.11 (D8); also elsewhere on the board
/DEVICES/LED1: A1.5 (D2); also elsewhere on the board
/DEVICES/LED2: A1.6 (D3); also elsewhere on the board
/DEVICES/MISO: A1.15 (D12); also elsewhere on the board
/DEVICES/MOSI: A1.14 (D11); also elsewhere on the board
/DEVICES/OLED_CS: A1.10 (D7); also elsewhere on the board
/DEVICES/OLED_DC: A1.12 (D9); also elsewhere on the board
/DEVICES/OLED_RST: A1.9 (D6); also elsewhere on the board
/DEVICES/SCK: A1.16 (D13); also elsewhere on the board
/DEVICES/SD_CS: A1.13 (D10); also elsewhere on the board
/DEVICES/SD_DETECT: A1.7 (D4); also elsewhere on the board
/MCU/EXT1: A1.20 (A1), J3.1; also elsewhere on the board
/MCU/EXT2: A1.21 (A2), J3.2; also elsewhere on the board
/MCU/EXT3: A1.22 (A3), J4.1; also elsewhere on the board
/MCU/EXT4: A1.8 (D5), J4.2; also elsewhere on the board
/MCU/bat_voltage: A1.19 (A0), R1.2, R2.1
/SCL: A1.24 (A5), J5.1, R10.2; also elsewhere on the board
/SDA: A1.23 (A4), J5.2, R11.2; also elsewhere on the board
GND: A1.4 (GND), A1.29 (GND), J3.4, J3.5, J3.6, J4.4, J4.5, J4.6, J5.4, J5.5, J5.6, R2.2; also elsewhere on the board

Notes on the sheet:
MCU NANO PINOUT ARDUINO NANO BLE 33
Référence https://content.arduino.cc/assets/NANO33BLE_V4.0_sch.pdf?_gl=1*1v2d5tn*_ga*MTgwOTc4MjI5MC4xNjg2OTY2OTQz*_ga_NEXN8H46L5*MTY4Njk3MDgyNi4yLjEuMTY4Njk3MTE2NC4wLjAuMA..
GROOVE EXTENSION
POWER

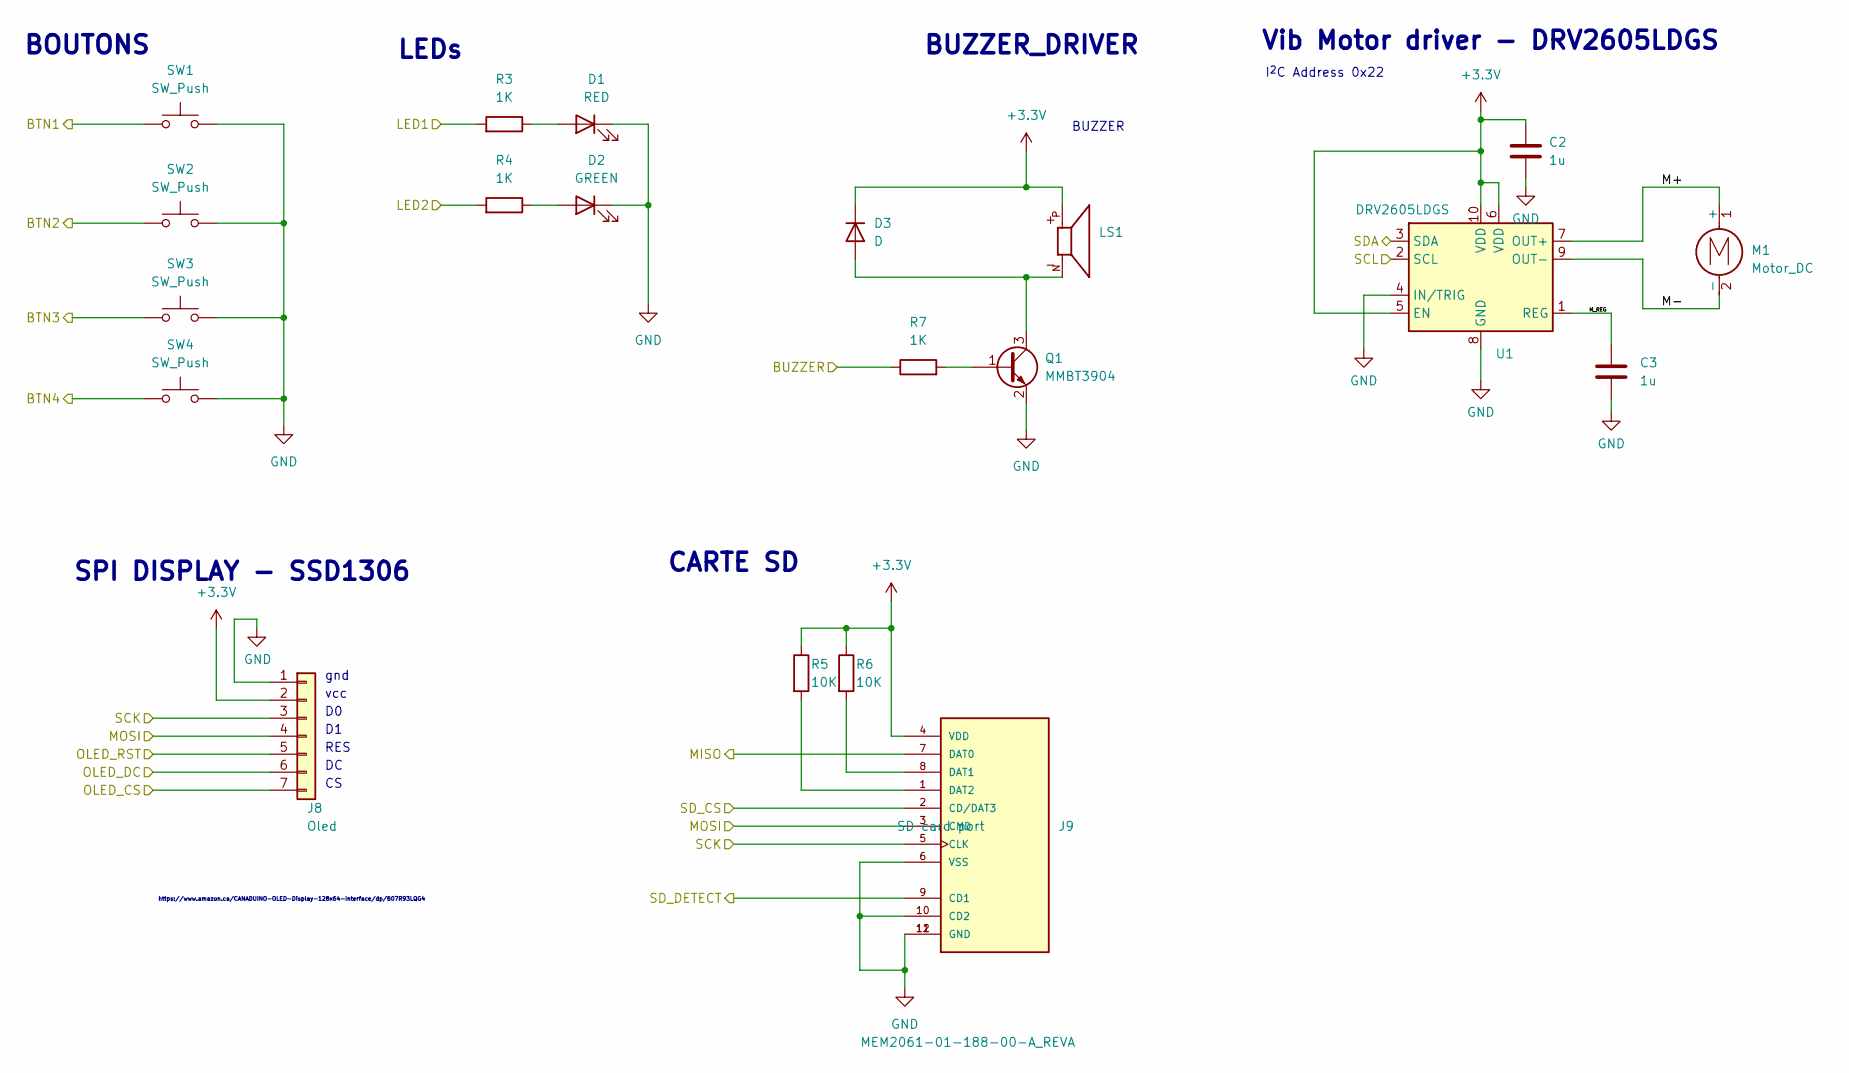
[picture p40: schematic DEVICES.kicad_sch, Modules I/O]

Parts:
C2, C3: 1u; C_0603_1608Metric; LCSC C15849
D1: RED; LED_D3.0mm; LCSC C779429
D2: GREEN; LED_D3.0mm; LCSC C2895476
D3: D; D_SOD-323F; LCSC C191023
J8: Oled; Adafruit_SSD1306_SPI; MPN AOM12864A0-0.96WW-ANO / ER-OLEDM0.96-1B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; Digikey AOM12864A0-0.96WW-ANO
J9: MEM2061-01-188-00-A_REVA; GCT_MEM2061-01-188-00-A_REVA; MPN MEM2061-01-188-00-A_REVA; LCSC C5151738
LS1: XDCR_CMT-7525-80-SMT-TR; LCSC C189208
M1: Motor_DC; XDCR_C0720B001F; MPN VC0720B001F
Q1: MMBT3904; SOT-23; LCSC C20526
R3, R4, R7: 1K; R_0603_1608Metric; LCSC C21190
R5, R6: 10K; R_0603_1608Metric; LCSC C25804
SW1, SW2, SW3, SW4: SW_Push; SW_SPST_TL3305B; LCSC C2939211
U1: DRV2605LDGS; VSSOP-10_3x3mm_P0.5mm; LCSC C527464

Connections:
+3.3V: C2.1, D3.1 (K), J8.2, J9.4 (VDD), LS1.P, R5.1, R6.1, U1.5 (EN), U1.6 (VDD), U1.10 (VDD); also elsewhere on the board
/DEVICES/BTN1: SW1.1; also elsewhere on the board
/DEVICES/BTN2: SW2.1; also elsewhere on the board
/DEVICES/BTN3: SW3.1; also elsewhere on the board
/DEVICES/BTN4: SW4.1; also elsewhere on the board
/DEVICES/BUZZER: R7.1; also elsewhere on the board
/DEVICES/LED1: R3.2; also elsewhere on the board
/DEVICES/LED2: R4.2; also elsewhere on the board
/DEVICES/M+: M1.1 (+), U1.7 (OUT+)
/DEVICES/M-: M1.2 (-), U1.9 (OUT-)
/DEVICES/MISO: J9.7 (DAT0); also elsewhere on the board
/DEVICES/MOSI: J8.4, J9.3 (CMD); also elsewhere on the board
/DEVICES/M_REG: C3.1, U1.1 (REG)
/DEVICES/OLED_CS: J8.7; also elsewhere on the board
/DEVICES/OLED_DC: J8.6; also elsewhere on the board
/DEVICES/OLED_RST: J8.5; also elsewhere on the board
/DEVICES/SCK: J8.3, J9.5 (CLK); also elsewhere on the board
/DEVICES/SD_CS: J9.2 (CD/DAT3); also elsewhere on the board
/DEVICES/SD_DETECT: J9.9 (CD1); also elsewhere on the board
/SCL: U1.2 (SCL); also elsewhere on the board
/SDA: U1.3 (SDA); also elsewhere on the board
GND: C2.2, C3.2, D1.1 (K), D2.1 (K), J8.1, J9.6 (VSS), J9.10 (CD2), J9.11 (GND), J9.12 (GND), Q1.2 (E), SW1.2, SW2.2, SW3.2, SW4.2, U1.4 (IN/TRIG), U1.8 (GND); also elsewhere on the board
unnamed: D1.2 (A), R3.1
unnamed: D2.2 (A), R4.1
unnamed: D3.2 (A), LS1.N, Q1.3 (C)
unnamed: J9.8 (DAT1), R6.2
unnamed: J9.1 (DAT2), R5.2
unnamed: Q1.1 (B), R7.2

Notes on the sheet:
BUZZER_DRIVER
I^{2}C Address 0x22
gnd
LEDs
vcc
Vib Motor driver - DRV2605LDGS
SPI DISPLAY - SSD1306
BOUTONS
RES
BUZZER
https://www.amazon.ca/CANADUINO-OLED-Display-128x64-Interface/dp/B07R93LQG4
CARTE SD

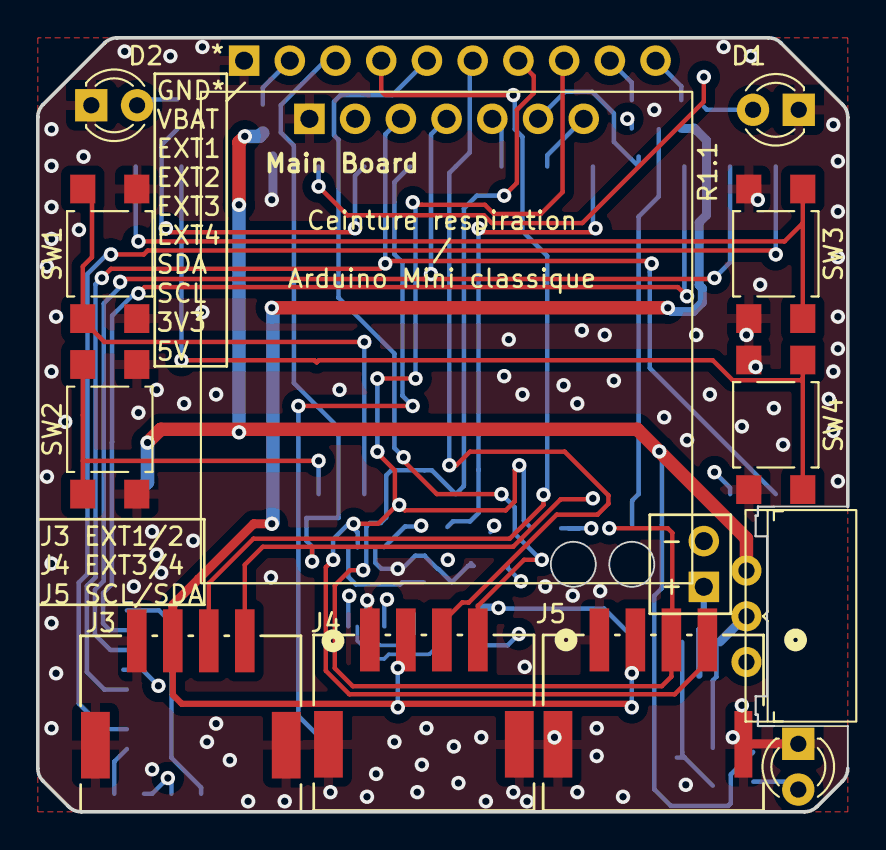
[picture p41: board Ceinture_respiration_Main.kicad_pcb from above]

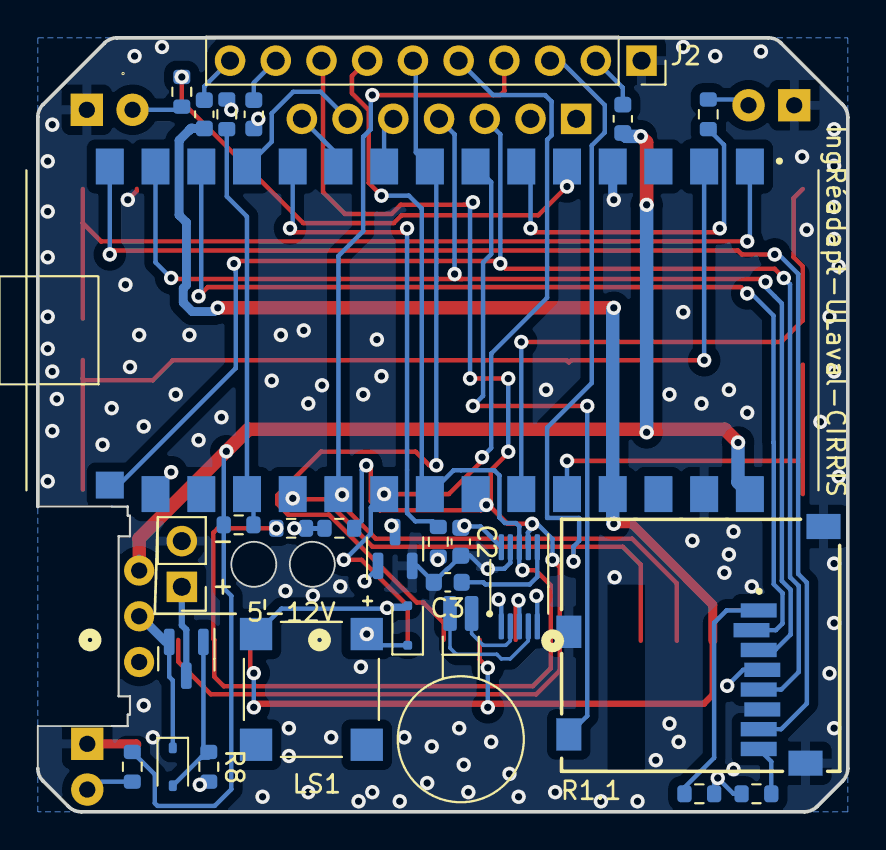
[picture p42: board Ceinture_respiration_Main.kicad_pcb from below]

Board: 4 copper layers, 45.0 x 43.0 mm, 39 parts (27 on the bottom side), 42 nets.

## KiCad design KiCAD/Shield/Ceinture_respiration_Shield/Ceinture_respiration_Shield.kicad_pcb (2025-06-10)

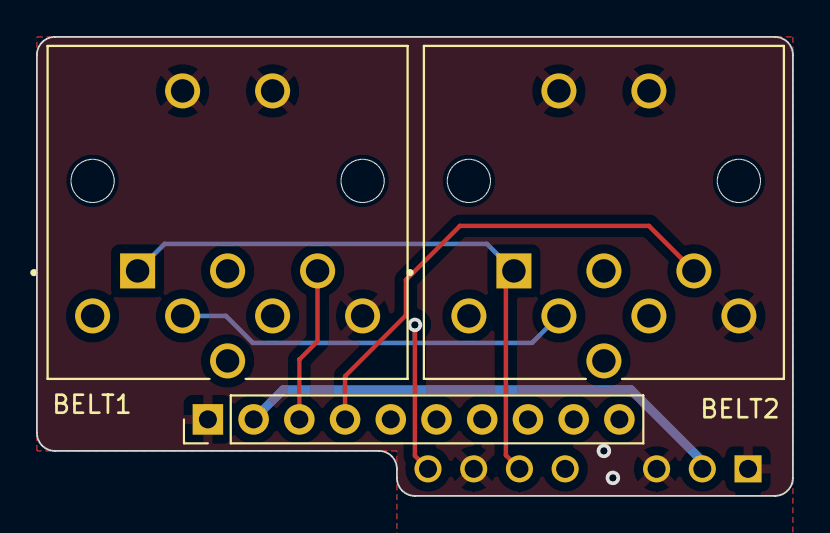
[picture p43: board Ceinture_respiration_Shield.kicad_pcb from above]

Board: 4 copper layers, 42.0 x 25.5 mm, 4 parts (1 on the bottom side), 6 nets.

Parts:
J1: Conn_01x10_Pin; PinHeader_1x10_P2.54mm_Vertical
J6, J7: DIN-8; CUI_SDS-80J
PS1: RS3-0505D; CONV_RS3-0505D

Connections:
+5VA: J6.1, J7.1, PS1.6 (+VOUT)
-5VA: J6.4, J7.4, PS1.8 (-VOUT)
/SHIELD_RESPIRATION/Belt_1: J1.3, J6.3
/SHIELD_RESPIRATION/Belt_2: J1.4, J7.3
/SHIELD_RESPIRATION/VBAT_EXP: J1.2, PS1.2 (+VIN)
GND_EXP: J1.1, J6.7, J7.7, PS1.1 (-VIN), PS1.3 (CTRL), PS1.7 (COM)

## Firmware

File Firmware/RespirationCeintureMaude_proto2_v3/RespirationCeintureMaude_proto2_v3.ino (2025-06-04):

float pourcentagesousseuil = 0.05;


/**
 * @file TeamAT_IMUFusion_metriques_ex7_nano33.ino
 * @author Alexandre Lecours, Simon Latour
 * @brief  Montre ergonomie, permet de monitorer l'angle du bras
 * @version 1.0.0
 * @date 2021-09-02
 * 
 * @copyright Copyright (c) 2021
 * 
 * 
 * 
 * ParasportEstimeVitesse_v6
 * MB 2023
 */

//#define DEBUG_MODE 

#ifdef  DEBUG_MODE
  #define CODE_VERSION "6.6.6" 
#else
  #define CODE_VERSION "1.0.1" 
#endif

#include <ArduinoBLE.h>

#include "teamATbasic_V1_1.h"

#include "TeamAT_Filters_v1_1.h"

#include "oledDisplayManager_V1_1.h"  // Oled Display Manager
Adafruit_SSD1306 display;

#include "at_plaformAbstraction_V1_1.h"
#include "ButtonPollingManager_V2.3.h"

#include "SD_LOGGER_V1_3.h"

#include "cli_v1_0.h" //Command Line Interpreter library

#include "montre_light_arduino_defines.h"
#include "hapticFeedback_arduino.h"

//TODO compléter plus tard #include "triggerManager.h"

 #include "teamtAt_deviceID_V1.0.h"
 #include "backupManager_Arduino_NFR52_V1.1.h"
 #include "backupData_ModuleErgonomie.h"



#include "menuPage_main.h" // The Drink Reminder Menu


/////////////////////////////////////////////////////////////////////////
// !!!!!! INITIALISATION !!!!!!
/////////////////////////////////////////////////////////////////////////

    /////////////////////////////////////////////////////////////////////////
    // General
    //  *** Keep what you need
    /////////////////////////////////////////////////////////////////////////
      // Global variables init
      
      long counter = 0;      // Counter used for data
      int firstloop = 0;    // Global variable used to detect the first pass in the loop

      #define SPI_FREQ 20//40//20       // Fréquence du bus SPI à utiliser
      #define LOG_SERIAL 0    // Log data on serial port
      #define LOG_SD 1        // Log data on SD card
      int logPreferedDest = LOG_SD;
      int SerialSD = logPreferedDest;  // By default, we log data on SD card.
  
    /////////////////////////////////////////////////////////////////////////
    // IO
    //  *** Garder ce que vous avez besoin
    /////////////////////////////////////////////////////////////////////////
      // Pinout
        #define LED_ON 1    // Leds are on "pull down" on the arduino board 
        #define LED_OFF 0 
        const int led_alert = led_alert_pin;//7boarddrinkremind;//5boardacl;// pin de la led   
        const int led_sd = led_sd_pin; // 6;//5boarddrinkremind;//6boardacl;
        const int inBatVoltage = IN_BAT_VOLTAGE;
        const int audioread = audioread_pin;
        int sensor1_pin = A1;
        int sensor2_pin = A2;
     // ------------------------------------------------------------------- //

  /////////////////////////////////////////////////////////////////////////
  // Specific to this algos
  //  *** Keep what you need
  /////////////////////////////////////////////////////////////////////////

      // Variables to manage fix frequency tasks 
      //  *** you can change the time interval with txIntervalMillis
      unsigned long currentMillisStart;
      unsigned long prevMillis50ms;
      unsigned long currentMillisEnd;
      unsigned long loopintervalMillis=0;
      unsigned long prevMillisTaks10ms=0;
      unsigned long prevMillisTaks1000ms=0;
      unsigned long debut_temps_alert =0;
      unsigned long fin_temps_alert =0;
      unsigned long temps_total_alert=0;
      float temps_total_alert_secondes=0;
      ///////////////////////////////////////////////////////////////////
      // VARIABLE 
      //////////////////////////////////////////////////////////////////
        // Ceinture respiration
        int sensor1ValueZero = 0;
        int sensor2ValueZero = 0;
        float ys1_filtHPLP_m1 = 0;
        float ys2_filtHPLP_m1 = 0;
        float ys1_filtHPLP = 0;
        float ys2_filtHPLP = 0;
        float ys12_filtHPLP = 0;
        float repos_expiratoire = 0;
        int val_s1_read = 0;
        int val_s2_read = 0;
        
        float maxvalue=0;
        float minvalue=25000;
        int last_button = 0;
        
        int initdone = 0;
        int initdone2 = 0;
        int sens_zero_counter = 0;

        float audioval = 0;

        int alertonoff = 1;
      ////////////////////////////////////////////////////////////////
        int buttonvalue = 0;
        int buttonvalue3 = 0;
        int alert = 0;
        int derniere_alert = 0;
        int alert_count = 0;
      ////////////////////////////////////////////////////////////////
      
      // *** Fixed frequency for our program ***
      long txIntervalMillis = 50; // 50ms
      int fs=20;//100;
  // ------------------------------------------------------------------- //

  // ------------------------------------------------------------------- //
  /////////////////////////////////////////////////////////////////////////
  // TEAMAT FEEDBACK
  /////////////////////////////////////////////////////////////////////////
    bool gHapticMode = MODE_ERM;
    hapticFeedback_arduino haptic; 

    
  /////////////////////////////////////////////////////////////////////////
  // OLED display I2C
  /////////////////////////////////////////////////////////////////////////
    #define DISPLAY_REFRESH_PERIOD  50    // Screen will be refreshed every 50 ms
    #define DISPLAY_SLEEP_TIME_MS   5000  // If sleep mode enable, the unit will go in sleep mode after 5000 ms

    // Instance of the display manager. The display manager as its name implies manages the display for you
    // making it easier and letting you concentrate of the tasks of you program
    //oledDisplayManager dispManager; 
  // ------------------------------------------------------------------- //
    

  /////////////////////////////////////////////////////////////////////////
  // Button Polling Manager
  /////////////////////////////////////////////////////////////////////////
    // Button polling Manager setup
    enum buttonIndexList{
      BUTTON_UP_INDEX,
      BUTTON_DOWN_INDEX,
      BUTTON_ENTER_INDEX,
      BUTTON_RETURN_INDEX,
      BM_NB_BUTTON 
    };
     managedButton buttonList[BM_NB_BUTTON] ={
      {IN_BUTTON_UP, NO_PORT, ACTIVE_LOW, CLICK_ENABLE | LONGCLICK_ENABLE}, 
      {IN_BUTTON_DOWN, NO_PORT, ACTIVE_LOW, CLICK_ENABLE | LONGCLICK_ENABLE}, 
      {IN_BUTTON_ENTER, NO_PORT, ACTIVE_LOW, CLICK_ENABLE | HOLD_ENABLE}, 
      {IN_BUTTON_RETURN, NO_PORT, ACTIVE_LOW, CLICK_ENABLE | HOLD_ENABLE} 

     };

     ButtonPollingManager buttonManager;
     void humanInputDeviceManagement();
     
  // ------------------------------------------------------------------- //

  /////////////////////////////////////////////////////////////////////////
  // Tone player
  // *** Comment all if no IMU. Or choose the number of IMU and ports.
  /////////////////////////////////////////////////////////////////////////
    #include "tonePlayer.h"
    tonePlayerClass tonePlayer; 

    
    // Init NRF52 timer NRF_TIMER3
    //#if ( ARDUINO_ARCH_NRF52840 && TARGET_NAME == ARDUINO_NANO33BLE )
    //  NRF52_MBED_Timer ITimer(NRF_TIMER_3);
    //#endif

  /////////////////////////////////////////////////////////////////////////
  // IMU
  // *** Comment all if no IMU. Or choose the number of IMU and ports.
  /////////////////////////////////////////////////////////////////////////
    #include "imu.h"
    // The SFE_LSM9DS1 library requires both Wire and SPI be included BEFORE including the 9DS1 library.
    #include <Wire.h>
    #include <SPI.h>
  
   // imuManagerClass imuManager; // Instance of the imu manager
  
    // IMU float data
    float imua_ax=0;float imua_ay=0;float imua_az=0;float imua_gx=0;float imua_gy=0;float imua_gz=0; //IMU 1
              
    #define NB_IMU 1      //Modify to select the number of actual IMUs you sish to use
    imuDataType imuData;
  
    // // Select IMU chip select (SD0 AG) digital IO attribution TABLE  *** Définir en fonction du nombre de IMU                
    //   // Chip select Table if usign Arduino board (CHANGE IF NEEDED):
    //   //  IMU 1 : Only device, no chip select
    //   //  IMU 2 : Not available
    //   //  IMU 3 : Not available
    //   int imuPinRef[NB_IMU_MAX] = {IMU_NO_CHIP_SELECT,
    //                                   IMU_NO_CHIP_SELECT,
    //                                   IMU_NO_CHIP_SELECT}; 

    
  // ------------------------------------------------------------------- //          


  /////////////////////////////////////////////////////////////////////////
  // SD CARD
  /////////////////////////////////////////////////////////////////////////
    bool log_onoff = false;              //Log On = true,Log Off = false  ( used to debounce button)
    int log_onOffInterrupt = false;     // Flag to communicate to the main loop that a button press was detected
    int last_log_onoff = -1;            // force detection of new state. on->off or off->on because some code only need to be executed
                                          // once when the logger is started or stopped.
    // SD chip select pin.  Be sure to disable any other SPI devices such as Enet.
       
    const uint8_t sdCardChipSelect = D10;  //SS1 pour MKRZero interne; SS pour autre; //SDCARD_SS_PIN pour ?;

 

    
    int flag_sdLogFileOpen=0; // Flag to indicate if the SD card has been initialized or not

  /////////////////////////////////////////////////////////////////////////
  // DATA Logger
  /////////////////////////////////////////////////////////////////////////
  // The data logger class is made to simplify logging data on SD card. byt taking care 
  // of the timing and communications for you. 
  /////////////////////////////////////////////////////////////////////////

  // * utilise sdfat.h qui est dans github\TeamAT_P_Arduino_MKRZero\SdFat. Devrait être dans le futur direct dans ce dossier.
    int loggindata = 0;
	#define logDataCount 10
    static char fileName[SDLOGGER_MAX_FILENAME_LEN];
    
    // Instance of the data logger
    //tow//sdlogger dataLogger;
    //tow//bool debug_newLineReceive = false;
    // Structure format for imu data logging
    struct __attribute__((packed)) datastore  // MB : modification des sorties
    {
       // int d_counter = 0;   // Data count
        int d_timestamp = 0; // Time in seconds
        float d_sensor1 = 0;    // float
        float d_sensor2 = 0;    // float
        float d_sensor12 = 0;    // float
        int d_alert = 0;
        float d_min = 0; // float
        float d_max = 0; // float
        float d_audio = 0; // float
        int d_alert_count = 0;
        float d_temps_total_alert_secondes=0;
        
        
    };

      char logDataTitles[logDataCount][32] = 
    					{
        "timestamp",
        "sensor1",
        "sensor2",
        "sensor12",
        "alert",
        "min",
        "max",
        "audio",
        "alert_count",
        "temps_total_alert_secondes"
    					};

    /*   
        char logDataTitles[logDataCount][32] =
              {
        "counter",
        "timestamp",
        "accx",
        "accy",
        "accz",
        "d_gyrx",
        "d_gyry",
        "accx_filt",//MB
        "d_Dist", //MB
        "d_speed1",
        "d_speed2",
        "d_Vit" //MB

              };*/
   uint8_t logDataTypes[logDataCount] =
					   {
					 //   logDataType_int,
              logDataType_int,
              logDataType_float,
              logDataType_float,
              logDataType_float,
              logDataType_int,
              logDataType_float,
              logDataType_float,
              logDataType_float,
				      logDataType_int,
              logDataType_float
                        };




    //  Because the data logger can be used for various data, it does not know
    //  the structure of the data you are using. You must specify in the following 
    //  callback function how to convert binary data to readable characters.
    //void logDataBinToChar(const uint8_t* binData, char* charData);
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

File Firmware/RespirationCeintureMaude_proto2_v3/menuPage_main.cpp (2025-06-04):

/**
 * @file DRMenu_main.cpp
 * @author Simon Latour
 * @brief Main menu page
 * @version 1.0
 * @date 2020-11-19
 * 
 * @copyright Copyright (c) 2020
 * 
 */

using namespace std;

#include "string.h"
#include "menuPage_main.h"
#include "readaptLogo.h"
#include "teamATbasic_V1_1.h"

// 'SOUND_on', 15x9px
const unsigned char icon_sound_on[] PROGMEM = {
    0x08, 0x10, 0x18, 0x48, 0x38, 0x24, 0xf9, 0x12, 0xf8, 0x92, 0xf9, 0x12, 0x38, 0x24, 0x18, 0x48,
    0x08, 0x10};
// 'sound_off', 15x9px
const unsigned char icon_sound_off[] PROGMEM = {
    0x08, 0x00, 0x1b, 0x0c, 0x39, 0x98, 0xf8, 0xf0, 0xf8, 0x60, 0xf8, 0xf0, 0x39, 0x98, 0x1b, 0x0c,
    0x08, 0x00};
// 'vibration', 15x9px
const unsigned char icon_vibration[] PROGMEM = {
    0xc0, 0x06, 0x60, 0x0c, 0x37, 0xd8, 0x64, 0x4c, 0xc4, 0x46, 0x67, 0xcc, 0x37, 0xd8, 0x60, 0x0c,
    0xc0, 0x06};

    // 'Bluetooth', 6x9px
const unsigned char icon_Bluetooth [] PROGMEM = {
	0x30, 0x28, 0xa4, 0x68, 0x30, 0x68, 0xa4, 0x28, 0x30
};


// Array of all bitmaps for convenience. (Total bytes used to store images in PROGMEM = 144)
const int icon_allArray_LEN = 4;
const unsigned char *icon_allArray[4] = {
    icon_sound_on,
    icon_sound_off,
    icon_vibration,
    icon_Bluetooth
    };

#define MAIN_DISPLAY_POS 10
#define TRAY_ORIGIN 0
#define SCREEN_MIN_SECTION (SCREEN_WIDTH_128 / 16)

#define TRAY_HEIGHT (SCREEN_MIN_SECTION * 2) // Reserve 1 section / 16  for tray

#define GLASS_SECTION_ORIGIN (TRAY_HEIGHT)
#define GLASS_SECTION_HEIGHT (SCREEN_MIN_SECTION * 6)

#define GOAL_SECTION_ORIGIN (GLASS_SECTION_ORIGIN + GLASS_SECTION_HEIGHT)
#define GOAL_SECTION_HEIGHT (SCREEN_MIN_SECTION * 6)

#define CONF_SECTION_ORIGIN (GOAL_SECTION_ORIGIN + GOAL_SECTION_HEIGHT)
#define CONF_SECTION_HEIGHT (SCREEN_MIN_SECTION * 2)

/**
 * Connect page with parent and menu manager
 * 
 * @param mManager is a pointer to the menu manager
 * @param parentMenu is apointer to the parent menu
 */
void menuPage_main::connect(menuManager *mManager, menu *parentMenu)
{
    //Connect this menu  to the menu manager and parent ( if any)
    m_menuManager = mManager;
    m_parentPage = parentMenu;

    //Connect sub menues to the menu manager and to this page an
    page_config.connect(m_menuManager, this);

    m_subMenuList[MAINSUB_CONFIG] = &page_config;
}

/**
 * @brief This functions connects to the display manager intance.
 * 
 * @param displayManager pointer tot he display manager
 */
void menuPage_main::connectDisplayManager(oledDisplayManager *displayManager)
{

    m_displayManager = displayManager;

    page_config.connectDisplayManager(displayManager);
    
}
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

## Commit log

2023-05-19 Basic Architecture and search of parts
    [CONNECTOR.kicad_sch, Ceinture Respiration.kicad_pcb, Ceinture Respiration.kicad_sch, DEVICES.kicad_sch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]
2023-06-22 First draft PCB and sch
    [ARDUINO_NANO.step.SLDASM, BH9VPC.step.SLDASM, COMPOUND-10.step.SLDPRT, COMPOUND-11.step.SLDPRT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]
2023-06-22 Cleanup files
    [CONNECTOR.kicad_sch, DEVICES.kicad_sch, MCU.kicad_sch, PSU.kicad_sch]
2023-07-21 Scématique complété
    Reste quelques footprint à configurer
    [Ceinture Respiration.kicad_sch, DEVICES.kicad_sch, MCU.kicad_sch, PWR_LIPO.kicad_sch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]
2023-07-21 Schématique prête pour design review
    [Ceinture Respiration.kicad_pcb]
2023-09-01 Schematique 99%, PCB 50%
    schématique complété, nettoyé et layout complété, reste routage
    [Ceinture Respiration.kicad_pcb, Ceinture Respiration.kicad_sch, DEVICES.kicad_sch, MCU.kicad_sch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]
2023-09-01 sch 99% pcb 85%
    Ajout de l'ensemble des traces du pcb mère
    Ajout de via stiching
    Reste le PCB shield à terminer
    Reste les erreurs générés à nettoyer
    Brûlé le gars...
    [Ceinture Respiration.kicad_pcb, PSU.kicad_sch]
2023-09-01 sch 99% pcb 99%
    Reste à préparer les commandes
    [Ceinture Respiration.kicad_pcb, Ceinture Respiration.kicad_sch, MCU.kicad_sch]
2023-09-01 PCB sent for production
    See latest production files.
    [Ceinture Respiration.kicad_pcb, Ceinture Respiration.kicad_sch, DEVICES.kicad_sch, MCU.kicad_sch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]
2023-09-23 Conception du boitier et documentation
    Boitier impression #2
    [9V-battery.SLDPRT, ARDUINO_NANO.step.SLDASM, AT0005-Case-Main.3MF, AT0005-Case-Main.SLDPRT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]
2023-10-15 Ajout version de case sans shield
    [9V-battery.SLDPRT, AT0005-Case-Main.3MF, AT0005-Case-Main.SLDPRT, AT0005-Case-Main.STL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]
2025-06-04 Ajout firmware Arduino
2025-06-09 SSéparé design en 2 pcb distinct
    [CONNECTOR.kicad_sch, Ceinture Respiration.kicad_pcb, Ceinture Respiration.kicad_sch, Ceinture_respiration_Main-CuBottom.gbr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]
2025-06-10 modifié info Part number du main board pour faciliter la génération de BOM non JLC
    [Ceinture_respiration_Main.kicad_sch, DEVICES.kicad_sch, MCU.kicad_sch, PSU.kicad_sch]
2025-06-10 Changé # pièce switch sur main board poru utiliser pièces en stock.
    [BOM - Non jlcpcb - Ceinture_respiration_Main.xlsx, Ceinture_respiration_Main-CuBottom.gbr, Ceinture_respiration_Main-CuIn1.gbr, Ceinture_respiration_Main-CuIn2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]
2025-06-10 ajouté fichiers oublier
    [BOM - non JLCPCB - Ceinture_respiration_Shield.csv, BOM-Ceinture_respiration_Main.csv, BOM-Ceinture_respiration_Shield.csv, CPL-Ceinture_respiration_Main.csv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]
2025-06-10 ajouté # de pièces option 2 de connectgeur batterie 9V
    [BOM - Non jlcpcb - Ceinture_respiration_Main.xlsx]
